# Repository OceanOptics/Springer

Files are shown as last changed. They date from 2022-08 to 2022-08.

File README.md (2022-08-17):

# Springer
Springer is an open source, side scattering optical sensor, utilizing commercially available electronics to measure water turbidity. We aim to create a low cost replicable sensor to be used for oceanographic research.
## Design
### Sensor Head
The sensor is designed for 3 LEDs and a Photodiode receiver. We have been testing LEDS with wavelengths of 650, 670, 720nm with plans to use a 490nm LED in conjunction with a red filter to measure phytoplankton fluorescence. Each LED is 90 degrees to the Photodiode receiver in the middle of the sensor. The head is built with scintillation vials in mind for quick testing and calibration purposes. The cap is designed to be screwed into the head for flow through measurements.

### Electronics
A transimpedance amplifier converts and amplifies current output from the Photodiode into a voltage output readable by an analog to digital converter.  The ADS1115 ADC module is used with an Arduino Nano to control and send data from the sensor to a computer. The signal readings for the three LEDs as well as a dark reading are processed and output by the Arduino through a converter to an RS232 serial bus. The LEDs are switched on and off using the Arduino's digital pins as well as three transistors in common-emitter configuration, allowing for multiple wavelengths to be sampled quickly. Power to the system is controlled by a voltage regulator which accepts input voltage from 7-24 volts.

### Printed Circuit Board
All electronic components are soldered directly to a custom built printed circuit board that can be ordered using the attached files from a variety of PCB manufacturers. A custom circuit board simplifies the design while ensuring all components are properly connected and grounded allowing for quicker assembly as well as a single removable plate that can easily be inserted into and removed from the housing. All components are soldered to the board using through hole pins.



### Housing & Waterproofing
A thick PVC is used as the main housing chamber for the sensor's electronic components. The Sensor head and end cap are attached to the main chamber using fitted O rings to ensure a tight waterproof seal. The sensor head optical pathways are made clear and waterproofed using an epoxy, and shaped using a silicone mold. This helps minimize optical deformities in the epoxy and keep electronics like the LEDs and photodiode sealed. Other 3D printed components are coated with epoxy to ensure no water is leaking into the system and helps improve the rigidity of the components. Wires are fed into the housing using a BLUE ROBOTICS wetlink penetrator.

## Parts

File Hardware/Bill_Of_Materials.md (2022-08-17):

| **Parts**              | part ID              | Quantity | Cost   | Supplier Reference                                                                                                                                |
|------------------------|----------------------|----------|--------|---------------------------------------------------------------------------------------------------------------------------------------------------|
| **Electronics**        |                      |          |        |                                                                                                                                                   |
| Arduino Nano           | ATmega328P           |        1 |     20 | https://www.digikey.com/en/products/detail/arduino/A000005/2638989                                                                                |
| ADC                    | ADS 1115             |        1 |     15 | https://www.digikey.com/en/products/detail/adafruit-industries-llc/1085/5761229                                                                   |
| Voltage regulator      | LM7805               |        1 |      1 | https://www.digikey.com/en/products/detail/onsemi/MC7805BTG/1481213                                                                               |
| 10µF Capacitor         |                      |        1 |   0.05 |                                                                                                                                                   |
| .1µF Capacitor         |                      |        2 |   0.05 |                                                                                                                                                   |
| 22pf Capacitor         |                      |        1 |   0.05 |                                                                                                                                                   |
| 670nm LED              |                      |        1 |   12.5 | https://www.thorlabs.com/thorproduct.cfm?partnumber=LED670L                                                                                       |
| 650nm LED              |                      |        1 |   12.5 | https://www.thorlabs.com/thorproduct.cfm?partnumber=LED645L                                                                                       |
| 720nm LED              |                      |        1 |      7 | https://www.digikey.com/en/products/detail/marktech-optoelectronics/MT5720-IR/7319589                                                             |
| Photodiode             | FDS 100              |        1 |     15 | https://www.thorlabs.com/thorproduct.cfm?partnumber=FDS100                                                                                        |
| Screw terminal         |                      |        4 |      1 | https://www.digikey.com/en/products/detail/cui-devices/TB010-508-03BE/10064143                                                                    |
| UART to RS232          | MAX3232              |        1 |    6.5 | https://www.sparkfun.com/products/11189                                                                                                           |
| Transistor             | 2N9304               |        3 |    0.5 | https://www.digikey.com/en/products/detail/micro-commercial-co/2N3904-AP/950399                                                                   |
| 5.1KΩ Resistor         |                      |        3 |   0.05 |                                                                                                                                                   |
| 100Ω Resistor          |                      |        3 |   0.05 |                                                                                                                                                   |
| 10MΩ Resistor          |                      |        1 |   0.05 |                                                                                                                                                   |
| 1.85KΩ Resistor        |                      |        1 |   0.05 |                                                                                                                                                   |
| OP AMP                 | TLC272               |        1 |   1.75 | https://www.digikey.com/en/products/detail/texas-instruments/TLC272BCP/374893                                                                     |
| Custom PCB             |                      |        1 |      3 | Any PCB manufacturer                                                                                                                              |
| **Housing**            |                      |          |        |                                                                                                                                                   |
| Thick Wall PVC         | 2 3/8" OD" 1.913" ID |   1/2 ft |        | https://www.mcmaster.com/pvc/thick-wall-plastic-pipe-for-water/                                                                                   |
| O ring                 | 1 7/8" OD 1.5" ID    |        4 |        | https://www.mcmaster.com/browse-sealing/o-rings/od~1-895/                                                                                         |
| Compression plug       | 7.5mm HC             |        1 |     12 | https://bluerobotics.com/store/cables-connectors/penetrators/wlp-vp/                                                                              |
| Epoxy                  |                      |          |        | https://www.amazon.com/dp/B086L1CDMT/?coliid=I2U3OUIO2NFCSK&colid=ZLDK1T27ULY5&psc=1&ref_=lv_ov_lig_dp_it                                         |
| Molding Silicone       |                      |          |        | https://www.amazon.com/dp/B07V5FFPWC/?coliid=I1ZYD7WM47C1VC&colid=ZLDK1T27ULY5&psc=1&ref_=lv_ov_lig_dp_it                                         |
| Acrylic Plastic cement |                      |          |      5 | https://www.amazon.com/SCIGRIP-10319-Acrylic-Cement-Low-VOC/dp/B0046768VS?source=ps-sl-shoppingads-lpcontext&ref_=fplfs&psc=1&smid=A10RWI7IMZFD50 |
|                        |                      | Total:   | 112.25 |                                                                                                                                                   |

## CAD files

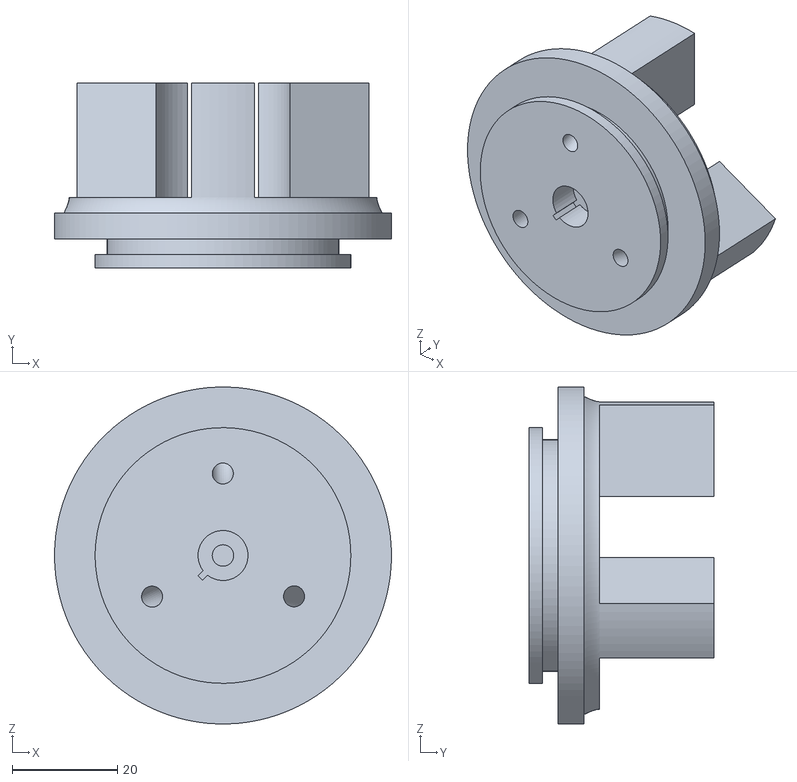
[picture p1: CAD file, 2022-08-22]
Print_Files/stl/Head Key.stl
64.0 x 35.2 x 64.0

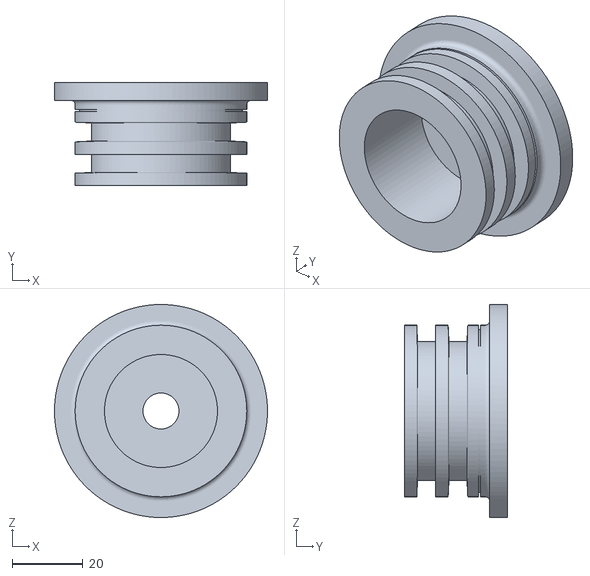
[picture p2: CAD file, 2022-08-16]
Print_Files/stl/EndCap.stl
60.3 x 29.2 x 60.3

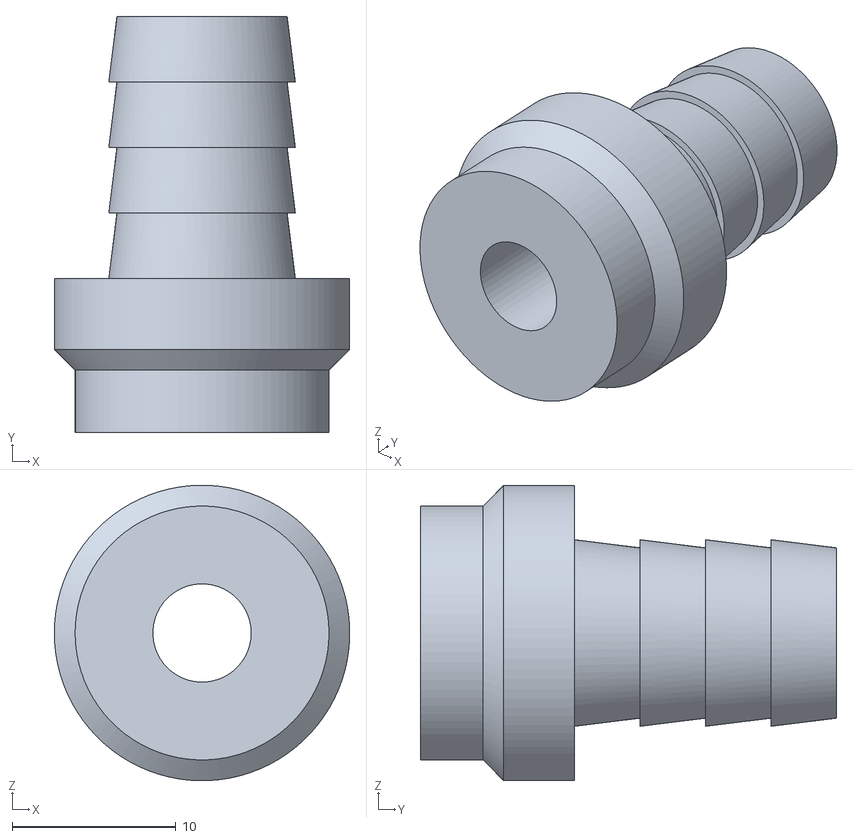
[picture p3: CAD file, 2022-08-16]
Print_Files/stl/hose.stl
18.0 x 25.4 x 18.0

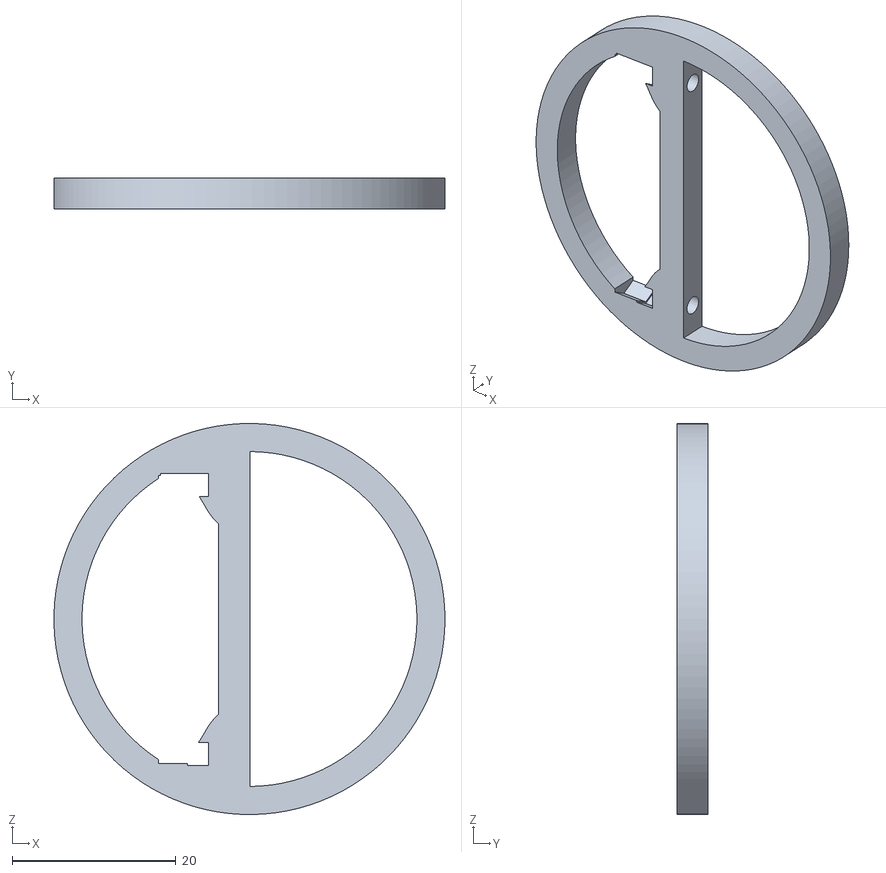
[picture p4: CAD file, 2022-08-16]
Print_Files/stl/Chassis.stl
47.7 x 3.81 x 47.7

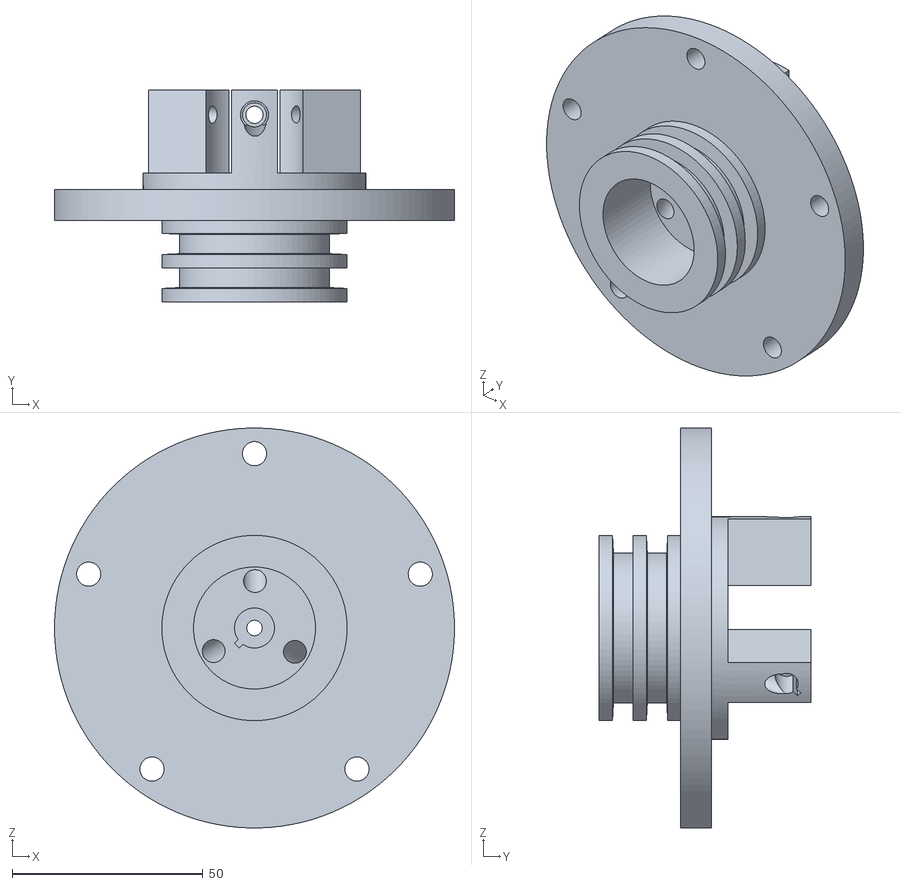
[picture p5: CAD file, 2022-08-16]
Print_Files/stl/Head.stl
104.9 x 55.5 x 104.9

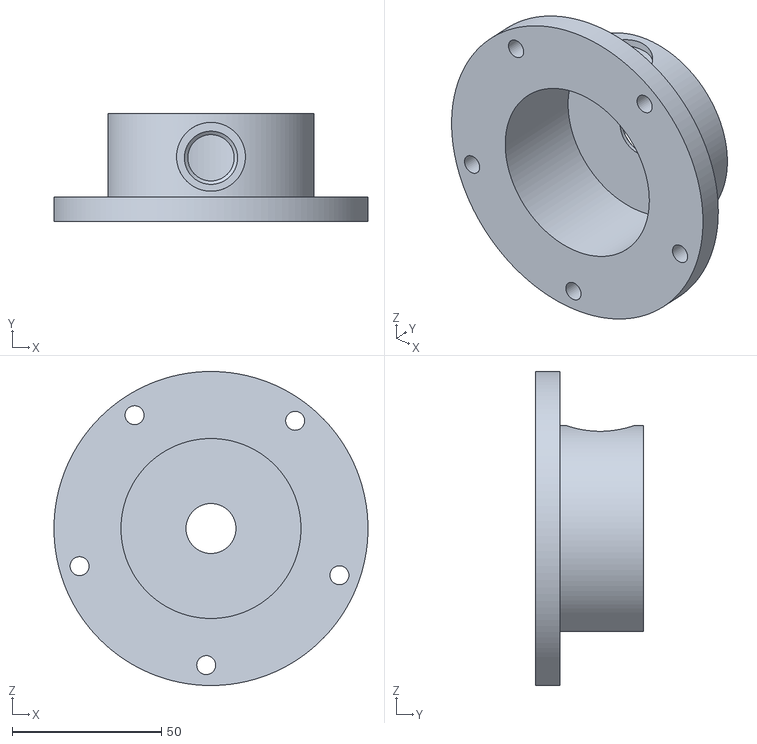
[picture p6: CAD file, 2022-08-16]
Print_Files/stl/Cap.stl
105.0 x 36.1 x 105.0

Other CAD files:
Print_Files/f3d/Springer CAD.f3d

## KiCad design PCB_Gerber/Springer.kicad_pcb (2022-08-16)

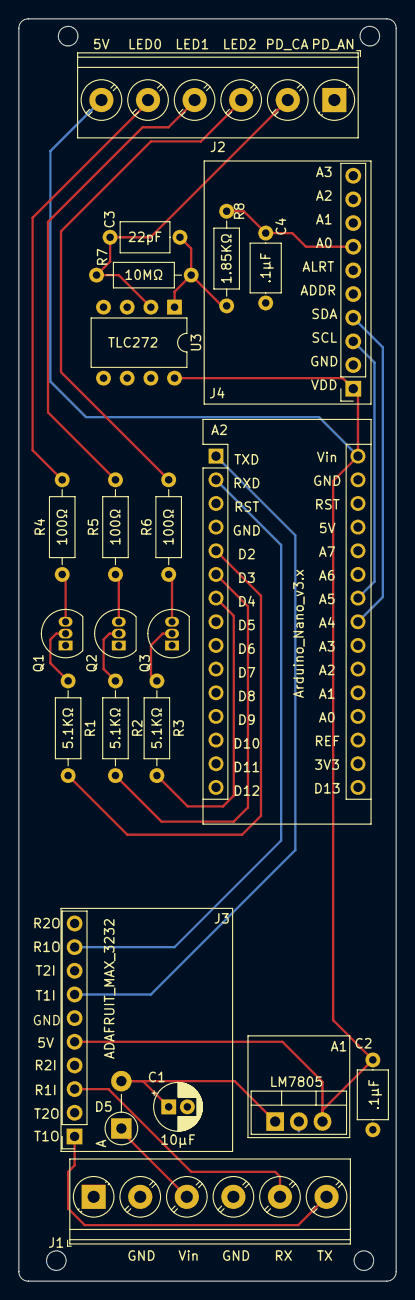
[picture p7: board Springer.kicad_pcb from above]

Board: 2 copper layers, 40.5 x 135.5 mm, 23 parts (0 on the bottom side), 25 nets.

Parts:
A1: LM7805; TO-220-3_Vertical
A2: Arduino_Nano_v3.x; Arduino_Nano
C1: 10µF; CP_Radial_D5.0mm_P2.00mm
C2, C4: .1µF; C_Axial_L5.1mm_D3.1mm_P7.50mm_Horizontal
C3: 22pF; C_Axial_L5.1mm_D3.1mm_P7.50mm_Horizontal
D5: DIODE; D_DO-41_SOD81_P5.08mm_Vertical_AnodeUp
J1, J2: Screw_Terminal_01x06; TerminalBlock_Phoenix_PT-1,5-6-5.0-H_1x06_P5.00mm_Horizontal
J3: ADAFRUIT_MAX_3232; PinSocket_1x10_P2.54mm_Vertical
J4: ADS1115; PinSocket_1x10_P2.54mm_Vertical
Q1, Q2, Q3: 2N3904; TO-92_Inline
R1, R2, R3: 5.1KΩ; R_Axial_DIN0207_L6.3mm_D2.5mm_P10.16mm_Horizontal
R4, R5, R6: 100Ω; R_Axial_DIN0207_L6.3mm_D2.5mm_P10.16mm_Horizontal
R7: 10MΩ; R_Axial_DIN0207_L6.3mm_D2.5mm_P10.16mm_Horizontal
R8: 1.85KΩ; R_Axial_DIN0207_L6.3mm_D2.5mm_P10.16mm_Horizontal
U3: TLC272; DIP-8_W7.62mm

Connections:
/5V: A1.3 (VO), A2.30 (VIN), C2.2, J2.6, J3.5, J4.1, U3.8 (V+)
/LED0: J2.5, R4.2
/LED1: J2.4, R5.2
/Rx: J1.5, J3.3
/Tx: J1.6, J3.1
/Vin: D5.1 (K), J1.3
GND: A1.2 (GND), A2.29 (GND), C1.2, C2.1, C4.2, J1.2, J1.4, J2.1, J3.6, J4.2, J4.5, Q1.1 (E), Q2.1 (E), Q3.1 (E), U3.3 (+), U3.4 (V-)
unnamed: A1.1 (VI), C1.1, D5.2 (A)
unnamed: A2.1 (D1/TX), J3.7
unnamed: A2.2 (D0/RX), J3.9
unnamed: A2.5 (D2), R1.2
unnamed: A2.6 (D3), R2.2
unnamed: A2.7 (D4), R3.2
unnamed: A2.23 (A4), J4.4
unnamed: A2.24 (A5), J4.3
unnamed: C3.2, R7.1, R8.1, U3.1
unnamed: C4.1, J4.7, R8.2
unnamed: C3.1, J2.2, R7.2, U3.2 (-)
unnamed: J2.3, R6.2
unnamed: Q1.2 (B), R1.1
unnamed: Q1.3 (C), R4.1
unnamed: Q2.2 (B), R2.1
unnamed: Q2.3 (C), R5.1
unnamed: Q3.2 (B), R3.1
unnamed: Q3.3 (C), R6.1

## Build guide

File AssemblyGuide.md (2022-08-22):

# Assembly Instructions

## PCB
###### Soldering:
Ensure all components have correct polarity and fit into the board. Reference soldering notes for tips with specific components.
###### Mounting :
Print two chassis rings and insert the PCB through the ring and screw the PCB down into the chassis.
## Head
###### 3D printing:
Using ABS filament, use the files on github to create gcode files that give instructions to the printer. This process is called slicing, there are many free online slicers to use for this process, as well as hosting the printer (controlling it). Standard ABS settings should work well for most printers, but for better quality changing height layers, amount and temperature can all give varying results. Ensure supports are on for all of the print files.
###### Silicone:
Mix parts A and B 1:1 by **weight** in a plastic cup. Mix for at least 3 minutes making sure to scrape the sides and bottom. Prepare the head key by taping over the areas where the LED’s and photodiodes are to ensure a smooth flat surface. Resin tape works well for this step. Use two sided tape to stick the head key print to the bottom of another cup. Pour epoxy over the key ~1 inch above the highest piece of plastic slowly. To allow any bubbles that may have formed to escape, seal the cup with saran wrap and put it in the fridge for 1 hour to slow the curing process and allow bubbles to escape. After, allow mold to cure in a dry room at room temperature. Let cure for at least 8 hours. Trim the top of the epoxy until you can remove the print. Using a small knife cut excess silicone until the head fits all the way in, be careful not to cut below the layer with the photodiode hole.
###### Epoxy:
Insert the head print into the silicone mold created by the key print in the above process. Mix parts A and B 1:1 by **volume** thoroughly for at least 3 minutes in a plastic cup making sure to scrape the bottom and sides. Pour epoxy slowly and in small amounts and wait some time between pouring to allow bubbles to escape and try to keep the wires elevated so they do not get stuck in the epoxy. Use a lighter or torch on the top surface of the epoxy to level the epoxy and remove bubbles be careful not to burn the wires. Let cure for 24 hours.
## Housing
###### Pipe:
 Cut pvc to desired size using a pvc cutter or hacksaw. 6" minimum. Try to keep a straight clean cut. 	
###### Head:
Add a bit of waterproof grease to the O rings and slip them into their grooves. Connect wires from the head to the pcb and slide the mounted PCB into the tube. Lastly push the head down into the tube, if the head has issues sliding in, try twisting the head slightly.
###### End Cap:
Insert the Wetlink Penetrator into the slot, slide the cable through the assembly and seal it according to blue robotics instructions. Allow slack in the cable and then connect to the ports on the PCB. Add a bit of waterproof grease to the O rings and slip them into their grooves. Push head into the tube.

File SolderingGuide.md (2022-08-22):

# Schematic


## Power Supply
Regulates input power and ensures safe and reliable voltages for components.
- ensure correct polarity of diode and 10µf capacitor.

LM7805 Pinout              | Capacitor polarity | Diode Polarity                                                                                                                           |
----------------------|--------|---------------------------------------------------------------------------------------------------------------------------------------------------|
|   |                      |          |                                                                                                                                                     

## Max 3232
Converts UART to RS232. Allows serial communication between sensor and computer.
-Check RX and TX pins. T1out and R1in to the screw terminal. T1in and R1out to the Arduino.

## Arduino
Microcontroller used to switch LEDs on and off as well as record and smooth data from the ADC.
-Check RX, TX and Digital pins.
| **Arduino Nano Pinout**              |
|---
| 

## Photodiode amplifier
 Transimpedance amplifier circuit to convert photodiode signal to voltage as well as amplify it before the ADC.
- 10MΩ and 22pf in parallel between 1in- and 1inOUT. PD cathode connects to 1in-. 1OUT goes to the low pass filter. *Make sure OpAmp is powered

## ADC
Analog-Digital Converter. Converts the analog voltage signal from the photodiode amplifier to a digital signal readable by the Arduino. SDA transfers data and SCL transfers clock information. A0 channel is what I have been using. You could theoretically use any channel. Ensure the input to the channel comes from the low pass filter after the capacitor.
## Transistor network
 Transistors are used in common emitter configuration as switches to allow the Arduino to control the current to power the LEDs. Pin 1 to GND, pin 2 comes from Arduino with 5.1KΩ, resistor pin 3 comes from LED negative terminal with 100Ω resistors.

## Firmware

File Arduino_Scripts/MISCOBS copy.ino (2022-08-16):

/*
  Test strings for serial monitor
  $OPENOBS*4A
  $SET,1616605996,10*7E
*/

/*TODO
*/

/*LIBRARIES
 *  The first three libraries are included in standard Arduino IDE installations
 *  The last three libraries should be be downloaded from github and installed manually.
 *  Additionally, the Adafruit_ADS1015 library requires the Adafruit_I2CDevice library, if you do not already have it.
 */
#include <Wire.h>               //standard library
#include <SPI.h>                //standard library
#include <Adafruit_ADS1X15.h>   //Version 2.2.0  https://github.com/adafruit/Adafruit_ADS1X15

/*
 *  CONFIGURATION SETTINGS
 */
 
//firmware data
#define pLED2 2
#define pLED1 3
#define pLED0 4 
#define NUM_SAMPLES 115
#define warm 100 

//58 = 50 samples

//communications vars
const int MAX_CHAR = 60;            //max num character in messages
char messageBuffer[MAX_CHAR];       //buffer for sending and receiving comms

//time settings
unsigned long millisTime;
long currentTime = 0;

byte LEDArray[] = {pLED0, pLED1, pLED2};
int bufferVal[]={0,0,0};
byte LEDArrayLength = sizeof(LEDArray)/sizeof(LEDArray[0]);
int16_t darkArray[NUM_SAMPLES];
int16_t lightArray[NUM_SAMPLES];
int16_t dark, darkSD = 0; 
int16_t LED0, LED1, LED2 = 0; 
int16_t LED0SD, LED1SD, LED2SD = 0; 
int collectedSample = 0; 

//ADC vars
Adafruit_ADS1115 ads;
int gain;

/* SETUP
 *  try to establish coms with GUI
 *  initiate components
 *  warm for settings or use default
 *  create text file
 */

void setup() {
  delay(100); //allow power to stabilize

  //if anything writes to these before started, it will crash.
  Serial.begin(115200);
  Serial.setTimeout(50);
  Wire.begin();

  
  //initialize the ADC
  ads.setGain(GAIN_TWO); //reset gain
  ads.begin(0x48);  // Initialize ads1115
  ads.setDataRate(RATE_ADS1115_860SPS); //set the sampling speed
  ads.readADC_SingleEnded(0); //throw one reading away. Seems to come up bad.
  Serial.println("initializing adc, reading...."+ads.readADC_SingleEnded(0));
  bool adc_init = ads.readADC_SingleEnded(0) != -1;
  //LED test sequence 
  for (int k=0;k<5 ;k++){
    for (int i = 0; i < LEDArrayLength; i++) {
    digitalWrite(LEDArray[i], HIGH);
    }
    delay(250);
    for (int i = 0; i < LEDArrayLength; i++) {
    digitalWrite(LEDArray[i], LOW);
    }
    delay(250);
  }
  dark = darkSample();
  
}

/* LOOP
 *  read sensor
 */

int counter = 1;
int16_t adc = 0;
double adc0;
float volts0;
int16_t LEDVal = 0; 
int32_t darkAvg = 0;
int16_t temp; 
int32_t sum=0; 

double darkSample(){
  for (int i = 0; i < LEDArrayLength; i++) {
    digitalWrite(LEDArray[i], LOW);
    }
  delay(warm);
  for (int i; i < NUM_SAMPLES;i++){
    darkArray[i] = ads.readADC_SingleEnded(0);
    sum+= darkArray[i];
  }
  dark = sum/NUM_SAMPLES;
  sum = 0;
  return dark;
}

double LEDSample(byte LED){
  digitalWrite(LED, HIGH);
  delay(warm);
  for (int i=0; i < NUM_SAMPLES;i++){
  lightArray[i] = ads.readADC_SingleEnded(0);
  sum+=lightArray[i];
  }
  digitalWrite(LED,LOW);
  LEDVal = sum/NUM_SAMPLES;
  sum = 0; 
  return LEDVal;
}

double calculateSD(int data[]) {
    float sum = 0.0, mean, SD = 0.0;
    int i;
    for (i = 0; i < 10; ++i) {
        sum += data[i];
    }
    mean = sum / 10;
    for (i = 0; i < 10; ++i) {
        SD += pow(data[i] - mean, 2);
    }
    return sqrt(SD / 10);
}

void loop() {
  temp = dark;
  dark = darkSample();
  darkAvg = (dark/2)+(temp/2)+(dark & temp & 1);
  darkSD = calculateSD(darkArray);
  LED0 = LEDSample(pLED0);
  LED0SD = calculateSD(lightArray);
  LED1 = LEDSample(pLED1);
  LED1SD = calculateSD(lightArray);
  LED2 = LEDSample(pLED2);
  LED2SD = calculateSD(lightArray);
  delay(58);
  sprintf(messageBuffer,"%05d,%05d,%05d,%05d,%05d,%05d,%05d,%05d,%05d",counter,LED0,LED0SD,LED1,LED1SD,LED2,LED2SD,darkAvg,darkSD);
  Serial.println(messageBuffer);
  counter++;
}
 

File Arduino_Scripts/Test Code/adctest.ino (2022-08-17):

/*LIBRARIES
 *  The first three libraries are included in standard Arduino IDE installations
 *  The last three libraries should be be downloaded from github and installed manually.
 *  Additionally, the Adafruit_ADS1015 library requires the Adafruit_I2CDevice library, if you do not already have it.
 */
#include <Wire.h>               //standard library
#include <SPI.h>                //standard library
#include <Adafruit_ADS1X15.h>   //Version 2.2.0  https://github.com/adafruit/Adafruit_ADS1X15

/*
 *  CONFIGURATION SETTINGS
 */
 
#define pLED2 2
#define pLED1 3
#define pLED0 4 
#define NUM_SAMPLES 1000

//communications vars
const int MAX_CHAR = 60;            //max num character in messages
char messageBuffer[MAX_CHAR];       //buffer for sending and receiving comms

//time settings
unsigned long millisTime;
long currentTime = 0;

//ADC vars
Adafruit_ADS1115 ads;
int gain;

/* SETUP
* Initialize ADC
 */

void setup() {
  delay(100); //allow power to stabilize

  //if anything writes to these before started, it will crash.
  Serial.begin(115200);
  Serial.setTimeout(50);
  Wire.begin();
  digitalWrite(pLED2, HIGH);
  
  //initialize the ADC
  ads.setGain(GAIN_ONE); 
  ads.begin(0x48); 
  ads.setDataRate(RATE_ADS1115_860SPS); 
  ads.readADC_SingleEnded(0);
  } 

/* LOOP
 *  read sensor
 */

int counter = 1;
double sval=0;
int16_t adc = 0;
double adc0;
float volts0;
static unsigned int averageValue0 = 0;
static unsigned char collectedSample = 0;

const int numReadings = 50; 
int readings[numReadings];
int readIndex = 0 ;
double total = 0; 
double average;

double smooth()  //Rolling average smoothing of continual ADC readings 
{
  total = total - readings[readIndex];
  readings[readIndex]= ads.readADC_SingleEnded(0);
  total = total + readings[readIndex];
  readIndex = readIndex + 1;
  if (readIndex>=numReadings) {
    readIndex=0;
  }
  average = total/numReadings;
  return average;
  }

void loop() {
  millisTime = millis();
  adc0 += ads.readADC_SingleEnded(0);
  if (++collectedSample >= 1) {
    adc0 /= 1;
    adc = smooth();
    sprintf(messageBuffer,"%05d,%05d,%05d",averageValue0,adc,averageValue0);
    Serial.println(messageBuffer);
    counter++;
    collectedSample=0;
    adc0 = 0;
  }
}
 

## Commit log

2022-08-16 add PCB, CAD and Arduino IDE files
    [Cap.stl, Chassis.stl, EndCap.stl, Head.stl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]
2022-08-16 add Correct KICAD Project folder for PCB and schematic
    [OBS-B_Cu.gbl, OBS-B_Cu.gbr, OBS-B_Mask.gbr, OBS-B_Mask.gbs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]
2022-08-16 Updated ReadME
    Added electronics, housing and pcb. next add code and more images/info.
2022-08-17 ReadMe Fix, bill of materials and Code edits
2022-08-22 Add assembly & soldering guide and head key.stl
    [Head Key.stl]
2022-09-02 Organizing - added a gitignore and an f3d file
    [Cap.stl, Chassis.stl, EndCap.stl, Head Key.stl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]
